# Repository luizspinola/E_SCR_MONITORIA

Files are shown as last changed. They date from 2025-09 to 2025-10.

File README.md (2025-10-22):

# PROJETO DE MONITORIA DE EXPERIMENTAL DE SISTEMAS DE CONTROLE REALIMENTADO

## OBJETIVO: Realizar o controle de temperatura e vazão de ar de um secador de cabelo convencional.

# Mudanças necessárias
Para realizar o controle de um secador de cabelo convencional, foi necessário realizar alterações em aspectos básicos do projeto atual, que consiste em controlar o fluxo de ar e temperatura atráves de controle de potência de, respectivamente, um cooler e uma resistência de chuveiro (ou lâmpada) via PWM.

O primeiro aspecto que deve ser pensado e, intuitivamente já se supõe, é sobre a alimentação do sistema. No projeto original, todas as fontes de alimentação são DC. Se resumem a alimentação proveniente do prórpio microcontrolador e das fontes de bancada do laboratório. Um secador de cabelo é um item utilizado comumente em tomadas, assim, decidimos alimentá-lo a partir da própria tomada (uma decisaão que futuramente foi repensada). O outro aspecto a ser pensado é a modelagem e a manufatura de estruturas para acoplar os sensores ao secador, como mostra a figura abaixo.

<p align="center">
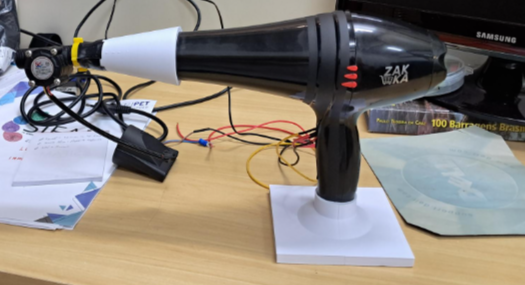
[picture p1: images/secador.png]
secador
  
</p>

Foram impressos um bocal, para conectar a saída de ar ao sensor de fluxo de ar, além de possuir um furo para que o sensor de temperatura seja inserido. Além disso, imprimiu-se uma base para que o secador ficasse em pé (as peças modeladas no Fusion podem ser encontradas na pasta CAD deste repositório).

# Desenvolvimento do projeto eletrônico

Diante das mudanças dos requerimentos do projeto, o esquemático abaixo foi desenvolvido, e verificado em _protoboard_ antes da confecção da PCB.

<p align="center">
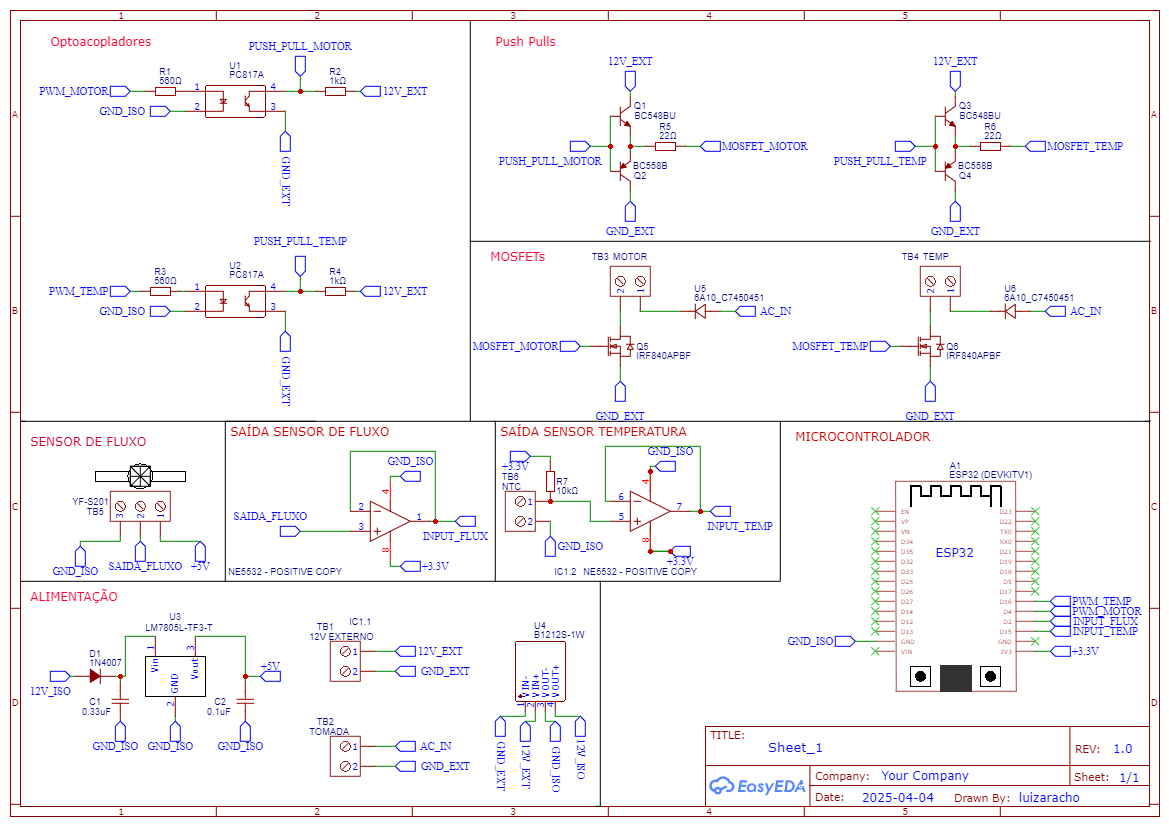
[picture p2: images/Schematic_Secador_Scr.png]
secador
  
</p>

Vamos por partes. O primeiro elemento a ser exposto são as cargas as quais devemos controlar a potência, isto é, precisamos realizar o controle de tensão sobre o motor do secador de cabelo (diretamente proporcional ao volume de ar que pode ser gerado) e sua resistência (diretamente proporcional a temperatura que o sistema pode atingir). A resistência não pode **sob hipótese nenhuma**, ser ligada quando o motor estiver desligado. Ao fazer isso, retira-se o principal e único dispositivo capaz de resfriar o secador de cabelo de maneira eficaz, podendo acometer na queima da resistência e perda deste componente.

Dessa forma, o desenvolvimento do esquemático foi dedicado a desenvolver uma placa que impeça a conexão e comunicação entre as malhas responsáveis pela alimentação destas cargas (maior potência) e pelo controle das mesmas cargas (menor potência), utilizando de componentes para isolar e separar o máximo possível estas fontes de tensão.

Note que, em basicamente cada zona do esquemático, temos duas cópias de um mesmo circuito, cada uma referente a cada uma das cargas que devemos controlar (motor e resistência do secador). A explicação de cada estágio do circuito vale para as duas cargas.

Primeiramente, antes de explicarmos os estágios do circuito de controle, é necessário deixar claro o que é necessário para construir um sistema de controle. Em suma, um elemento físico precisa de um dispositivo capaz de regular sua potência a partir de um certo acionamento. Em um carro, a velocidade é regulada pelo quanto de combustível é permitido acessar o motor, a partir do acionamento de uma válvula conectada aos cilindros de potência do carro. De forma que quando o carro está abaixo da velocidade, há um fluxo de óleo no cilindro de tal forma que a válvula suba e permita a passagem de um maior volume de combustível, aumentando a valocidade real (a recíproca é verdadeira). No caso de sistemas eletrônicos (como é o nosso), o combustível do motor pode ser tanto uma tensão quanto corrente elétrica aplicada, e cabe a nós encontrar ferramentas que permitam diminuir ou aumentar o fornecimento de combustível" a partir de um acionamento. No nosso caso, ao invés de conectar a alimentação diretamente sobre a carga, adiciona-se um transistor de tal maneira que, para que haja uma tensão na carga, a base do transitor deve estar polarizada e permitindo a passagem de corrente elétrica entre coletor e emissor. Isto é, O controle é realizado através da utilização de um transistor como um elemento de chaveamento. Caso a base do transistor sempre esteja polarizada, a carga estará "recebendo" o máximo de potência possível do sistema, se a base não for polarizada, a carga "receberá" potência nenhuma. Podemos regular a porcentagem de potência fornecida a carga modulando o sinal responsável pela polarização do transistor. Por isso é utilizado o PWM -_Pulse Width Modulation_. Entenda mais sobre PWM neste [link](https://www.youtube.com/shorts/xqR8hdYKgJs)   

## Estágio 1: Optoacopladores

<p align="center">
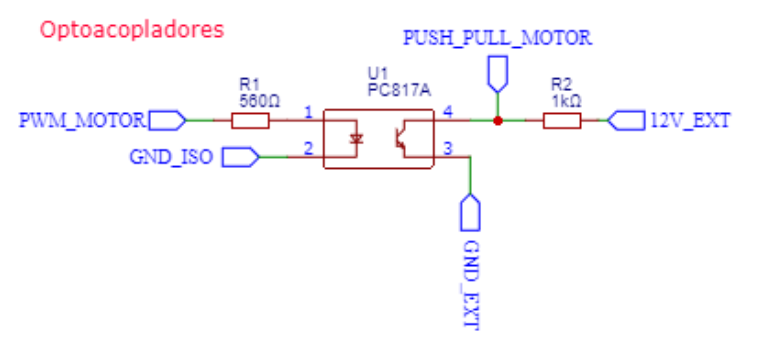
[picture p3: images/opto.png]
opto
  
</p>

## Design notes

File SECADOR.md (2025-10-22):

# PROJETO DE MONITORIA DE EXPERIMENTAL DE SISTEMAS DE CONTROLE REALIMENTADO

🧠: Texto escrito sem o auxílio de inteligência artificial

🤖: Texto escrito com o auxílio de inteligência artificial

## OBJETIVO: Realizar o controle de temperatura e vazão de ar de um secador de cabelo convencional.

# Mudanças necessárias
🧠 Para realizar o controle de um secador de cabelo convencional, foi necessário realizar alterações em aspectos básicos do projeto atual, que consiste em controlar o fluxo de ar e temperatura atráves de controle de potência de, respectivamente, um cooler e uma resistência de chuveiro (ou lâmpada) via PWM.

O primeiro aspecto que deve ser pensado e, intuitivamente já se supõe, é sobre a alimentação do sistema. No projeto original, todas as fontes de alimentação são DC. Se resumem a alimentação proveniente do prórpio microcontrolador e das fontes de bancada do laboratório. Um secador de cabelo é um item utilizado comumente em tomadas, assim, decidimos alimentá-lo a partir da própria tomada (uma decisaão que futuramente foi repensada). O outro aspecto a ser pensado é a modelagem e a manufatura de estruturas para acoplar os sensores ao secador, como mostra a figura abaixo.

<p align="center">
  secador
</p>

Foram impressos um bocal, para conectar a saída de ar ao sensor de fluxo de ar, além de possuir um furo para que o sensor de temperatura seja inserido. Além disso, imprimiu-se uma base para que o secador ficasse em pé (as peças modeladas no Fusion podem ser encontradas na pasta CAD deste repositório).

# Desenvolvimento do projeto eletrônico

🧠 Diante das mudanças dos requerimentos do projeto, o esquemático abaixo foi desenvolvido, e verificado em _protoboard_ antes da confecção da PCB.

<p align="center">
  secador
</p>

Vamos por partes. O primeiro elemento a ser exposto são as cargas as quais devemos controlar a potência, isto é, precisamos realizar o controle de tensão sobre o motor do secador de cabelo (diretamente proporcional ao volume de ar que pode ser gerado) e sua resistência (diretamente proporcional a temperatura que o sistema pode atingir). A resistência não pode **sob hipótese nenhuma**, ser ligada quando o motor estiver desligado. Ao fazer isso, retira-se o principal e único dispositivo capaz de resfriar o secador de cabelo de maneira eficaz, podendo acometer na queima da resistência e perda deste componente.

Dessa forma, o desenvolvimento do esquemático foi dedicado a desenvolver uma placa que impeça a conexão e comunicação entre as malhas responsáveis pela alimentação destas cargas (maior potência) e pelo controle das mesmas cargas (menor potência), utilizando de componentes para isolar e separar o máximo possível estas fontes de tensão.

Note que, em basicamente cada zona do esquemático, temos duas cópias de um mesmo circuito, cada uma referente a cada uma das cargas que devemos controlar (motor e resistência do secador). A explicação de cada estágio do circuito vale para as duas cargas.

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

## Estágio 1: Optoacopladores

<p align="center">
  opto
</p>

🤖 O optoacoplador é usado para isolar eletricamente dois circuitos, permitindo a transferência de sinais entre eles sem contato elétrico direto. O funcionamento baseia-se na conversão de um sinal elétrico em luz e, em seguida, novamente em um sinal elétrico. Internamente, o PC817A possui um LED emissor de infravermelho e um fototransistor. Quando uma corrente flui entre os pinos 1 (ânodo) e 2 (cátodo), o LED emite luz infravermelha. Essa luz incide sobre a base do fototransistor interno, que está entre os pinos 3 (emissor) e 4 (coletor). Assim, quando o LED está aceso, o fototransistor conduz, permitindo a passagem de corrente entre seus terminais. Quando o LED está apagado, o fototransistor permanece em corte, bloqueando o sinal.

🧠 A natureza do nosso sistema já explica por si só por que este componente é necessário, podemos separar o nosso esquemático em duas malhas de magnitudes distintas, uma malha de potência, em que a principal fonte de tensão é a tomada (AC) de 127V, e uma malha de controle, em que as principais fontes são a fonte de bancada, de 12V DC, além dos 3.3V fornecidos ao microcontrolador pela porta USB do _notebook_. Para evitar que tanto o microcontrolador, amplificador operacional, sensores e o _notebook_ sofram uma sobretensão que possa estragar estes componentes, é necessário isolar eletricamente estas malhas. 

## Alimentação e Fonte Isolada

<p align="center">
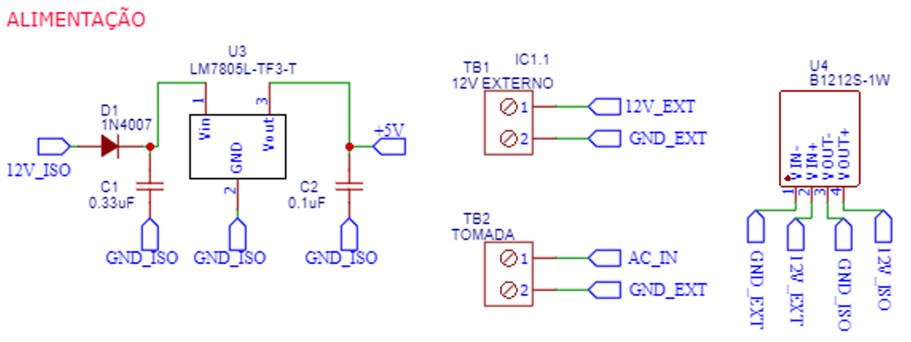
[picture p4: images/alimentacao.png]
fonte
  
</p>

A alimentação, exposta na última seção, possui um elemento que deve ser citado: A fonte isolada. Para que o acionamento e por consquência, o controle, funcione, tanto a malha de controle quanto a malha de potência precisam estar sobre a mesma referência. A mesma precaução que explica o uso do optoacoplador também justifica o motivo de não conectar os terras das duas malhas. Por isso, o componente U4, é responsável por deixar ambas malhas na mesma referência.

## Estágio 2: Push-Pulls

<p align="center">
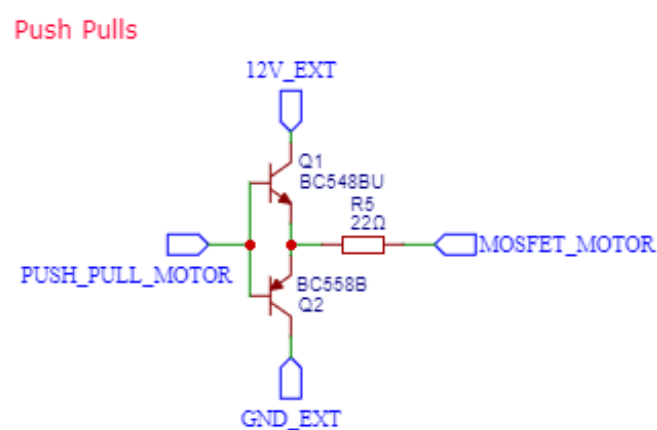
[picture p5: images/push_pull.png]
push
  
</p>

🤖🧠 O circuito push-pull opera como um driver de corrente de alta eficiência, utilizando um par de transistores complementares (NPN Q1 e PNP Q2) conectados de forma que suas bases sejam controladas por um sinal de entrada único e seus emissores estejam ligados à saída. Este circuito permite o fornecimento e absorção de corrente ativamente, resultando em uma comutação rápida da tensão de saída entre as fontes de alimentação, sendo ideal para acionar cargas que requerem alta corrente, como a porta de um MOSFET (como é o nosso caso).

🧠 Após a amplificação da corrente de saída do optoacoplador, este sinal vai para a porção do circuito que realmente controla o motor do secador.

## Estágio 3: MOSFET

<p align="center">
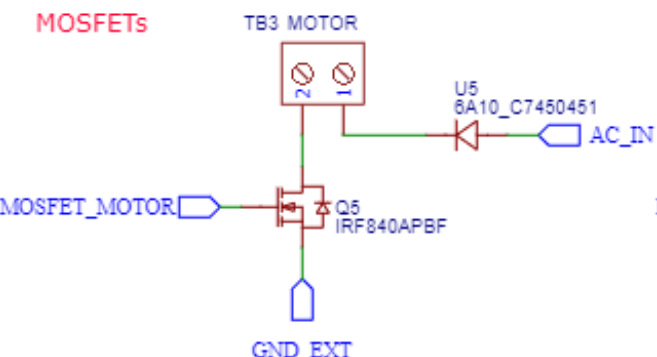
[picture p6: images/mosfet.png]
mosfet
  
</p>

🧠 Este circuito funciona da mesma maneira como foi explicado no parágrafo antes do estágio 1. A alimentação de meia onda alternada da tomada só é fornecida a carga (motor do secador) quando o _gate_ do mosfet for acionado. Em tese, essa configuração permitiria o controle de potência, porém, não foi o que aconteceu.

## Por que deu errado?

Ao iniciar os testes, percebeu se que, mesmo ao alterar o _duty cycle_ do sinal PWM, a variação de potência era imperceptível, mesmo diminuindo a frequência do pwm a uma múltipla dos 60Hz da rede. Após realizar testes com uma alimentação DC, ao invés de AC, percebemos que o erro se deu por conta de não nos atentarmos as propriedades físicas do próprio motor. Podemos ver isto na imagem abaixo. 

<p align="center">
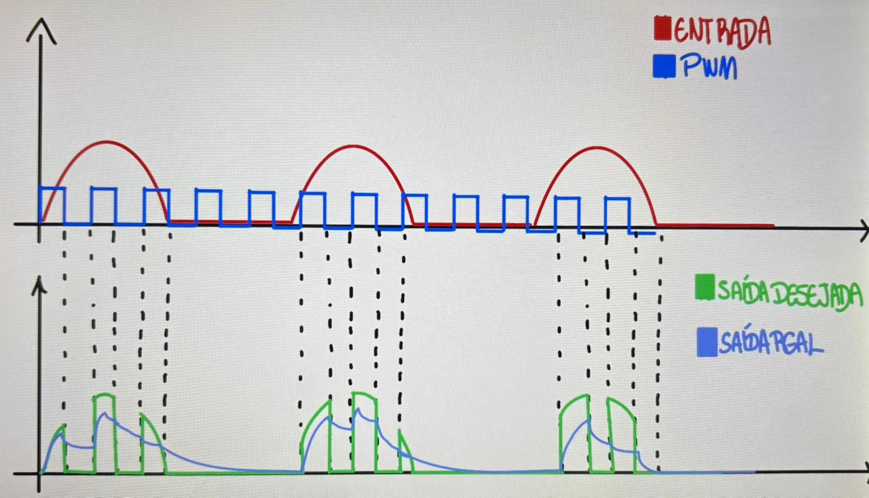
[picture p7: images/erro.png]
erro
  
</p>

O sinal de saída esperado na carga (em verde) deveria ser o mais próximo de uma réplica do sinal de entrada quando o nível lógico do PWM fosse alto. Isso seria verdadeiro caso estivéssemos lidando com uma carga puramente resistiva. Todavia, como já sabemos, motores de corrente alternada não são cargas puramente resistivas. Pelo contrário, seu princípio de funcionamento se sustenta pelo fato de seu material possuir reatâncias capacitivas e indutivas. Dessa maneira, a tensão no motor não atinge seu valor máximo e mínimo de imediato no instante de mudança de nível lógico do PWM, mas sim, aumenta e diminui em uma progressão exponencial (assim como o carregamento e descarregamento de um capacitor, por exemplo). Ou seja, na frequência trabalhada, "não dava tempo" para que a tensão no motor atingisse seu valor máximo e mínimo antes que sua alimentação fosse modificada, independente do ciclo de trabalho do PWM, assim, mantendo uma potência quase constante. A constatação deste fato veio, pelo menos, com uma solução possívelmente encontrada, ao pegar uma fonte de bancada e configurá-la em série, pude alimentar o motor com 60V DC, realizando uma variação de tensão na própria fonte, foi perceptivo a variação de potência, utilizando esta fonte e o circuito convencional do projeto (com _cooler_), adequando os componentes a esta nova faixa de operação, acredito que possa ser possível realizar este controle sem precisar de sofisticar ainda mais este esquemático que fiz.

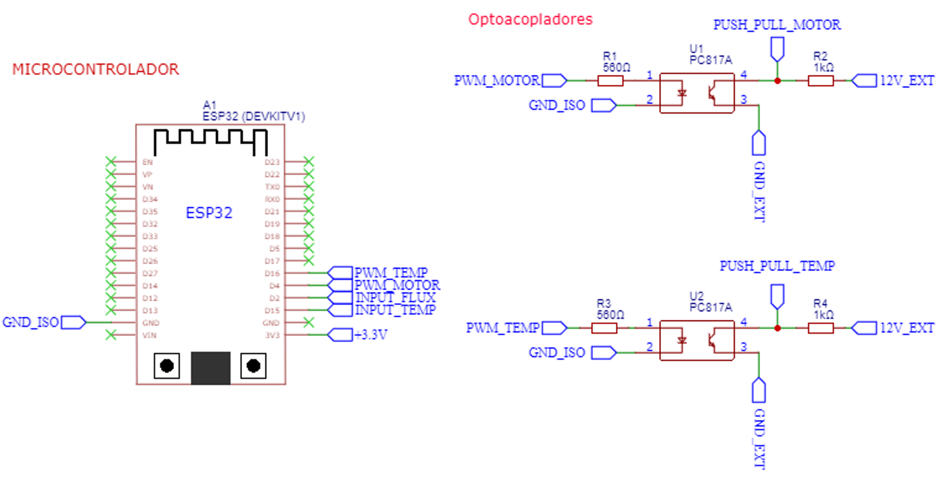
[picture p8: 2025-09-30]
images/esp_opto.png

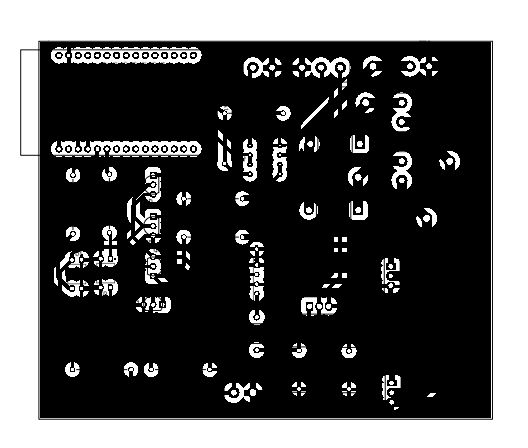
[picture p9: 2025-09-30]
images/PCB_PCB_SECADOR-SCR_3_2025-09-30.png

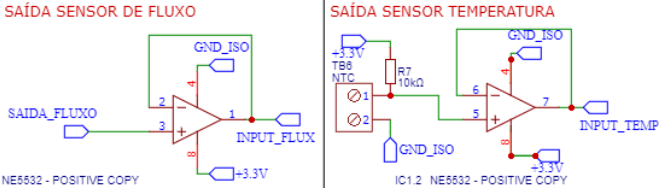
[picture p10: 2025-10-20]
images/AOs.png

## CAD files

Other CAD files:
CAD/base secador v4.f3d
CAD/bocal secador v4.f3d

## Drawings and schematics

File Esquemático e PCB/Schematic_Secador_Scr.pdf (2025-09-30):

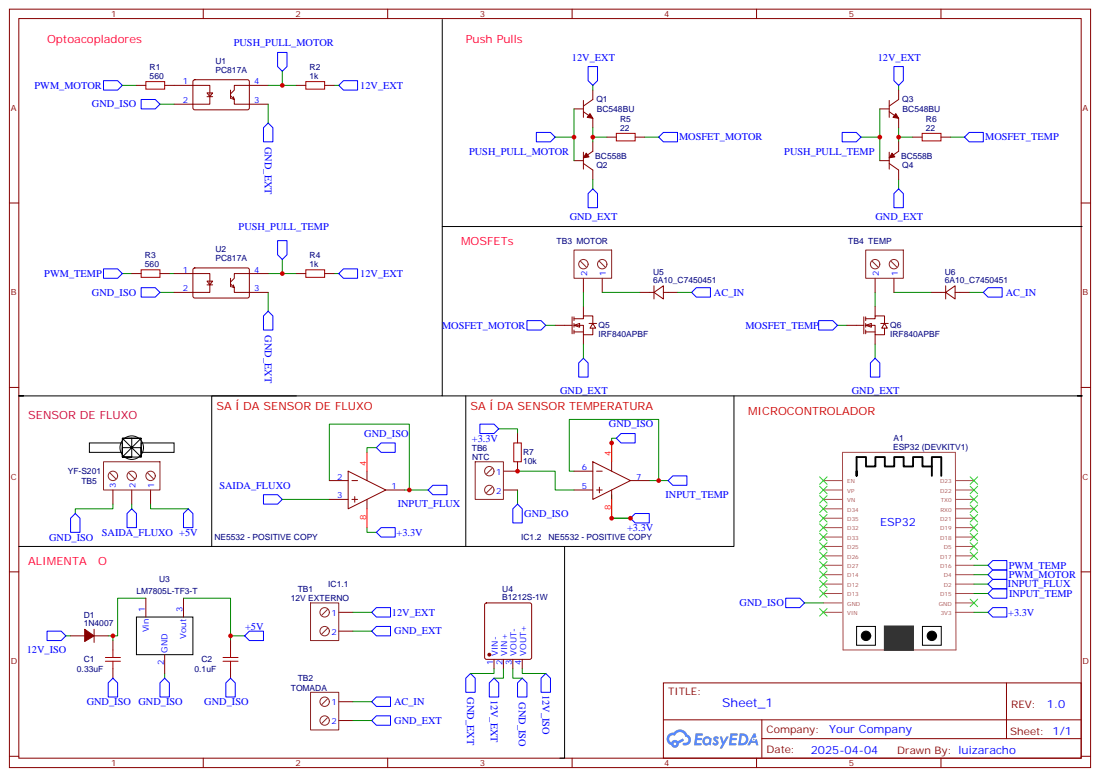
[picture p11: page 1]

SA DA SENSOR DE FLUXO

SA DA SENSOR TEMPERATURA

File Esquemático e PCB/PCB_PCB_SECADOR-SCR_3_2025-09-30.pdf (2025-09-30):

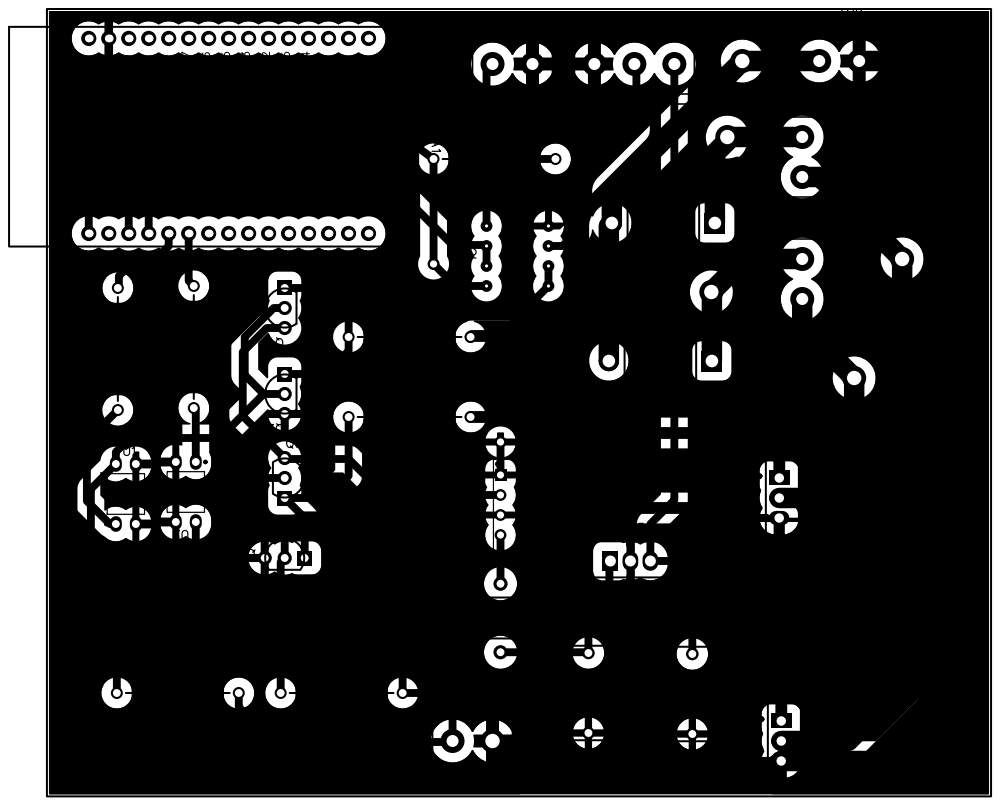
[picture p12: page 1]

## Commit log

2025-09-29 Update README with power supply information
    Clarify power supply details for hair dryer control project.
2025-09-29 cad added
    [base secador v4.f3d, bocal secador v4.f3d]
2025-09-29 Update README with power supply and sensor details
    Added details about power supply and structure for sensors.
2025-10-20 Expand README with circuit control stages
    Added explanation about the circuit stages and optoacouplers.
2025-10-22 Expand SECADOR.md with Push-Pull and MOSFET stages
    Added sections on Push-Pull stage and MOSFET stage, explaining their roles in the circuit and including images.
2025-10-22 Update SECADOR.md with circuit explanation
    Add explanation about the circuit operation and its failure.
2025-10-22 Add section on isolated power supply and control
    Adiciona seção sobre alimentação e fonte isolada, explicando a necessidade de manter as malhas de controle e potência isoladas. Inclui imagens para melhor compreensão.
2025-10-22 Atualiza seção sobre falhas no controle de potência
    Explicação sobre os testes realizados com o motor do secador e as limitações encontradas ao usar PWM para controle de potência.
2025-10-22 Enhance motor PWM control explanation in SECADOR.md
    Expand the explanation of motor behavior under PWM control and provide insights from testing with a bench power supply.
